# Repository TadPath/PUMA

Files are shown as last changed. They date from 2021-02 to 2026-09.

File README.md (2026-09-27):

PUMA 3D PRINTED MULTIMODALITY MICROSCOPE 
========================================

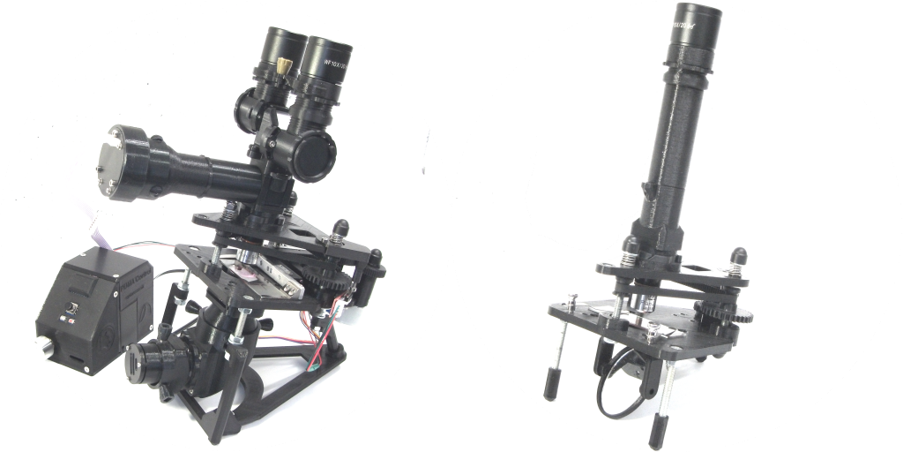
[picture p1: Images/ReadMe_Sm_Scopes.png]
PUMA Example Scopes

---

# **New** :arrow_right: **CNC Stage** 

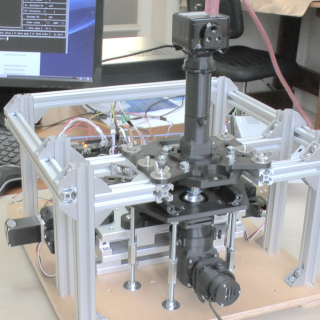
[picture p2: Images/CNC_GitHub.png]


I developed a full XYZ precision CNC stage for PUMA (completed in 2026) and I will be making videos to show you how you can make and use it. The CNC stage uses a 'standard' CNC system i.e. NEMA bipolar motors, optical limit switches, TMC2209 digital stepper drivers on a modified RAMPS 1.4 board (as opposed to 'custom PCBs'), desktop computer control with a 'standard' CNC breakout board (as opposed to being dependent on the RPi), ability to use 'standard' CNC software like Marlin, Klipper, GRBL, Linux CNC, etc. - but also controllable by my own [PARDUS control system](https://codeberg.org/TadPath/PARDUS).<br/>
If you want to follow the progress of this then [head over to the latest posts on my Patreon page](https://www.patreon.com/c/PUMAMicroscope).<br/>
<br/>
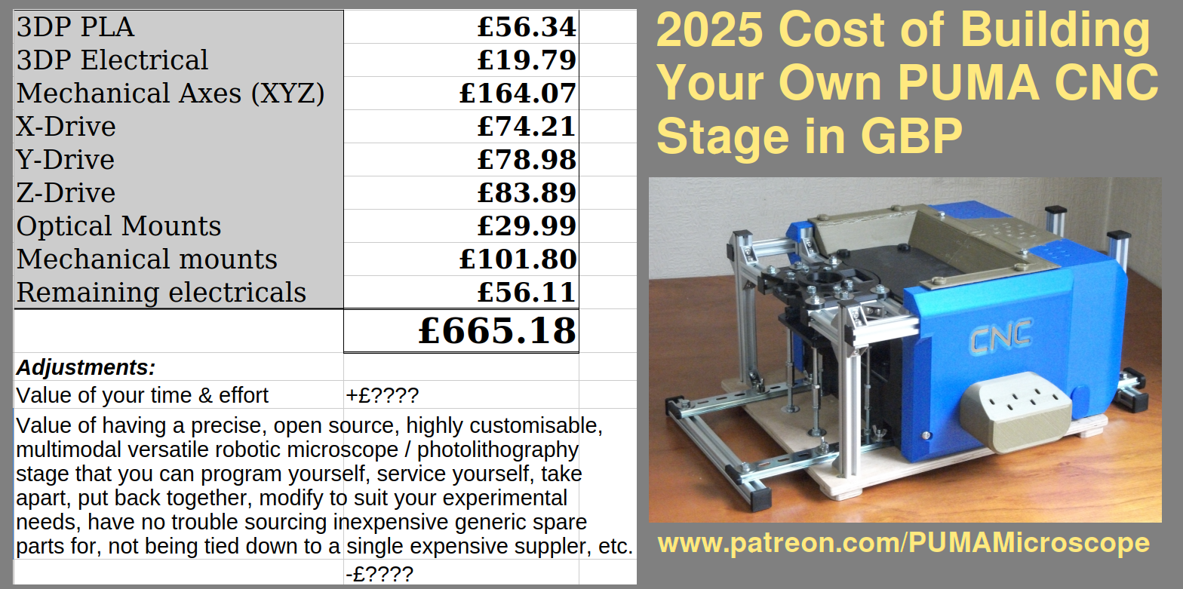
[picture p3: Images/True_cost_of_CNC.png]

<br/>

----------------------------------------------------------------

## :warning: **NOTE TO ALL MAKERS**

The 2021 (v.1.0.0) release is out of date - only use models from the main branch if building a scope. Also, the latest (v1.0 RC ) version of FreeCAD has bugs which make it difficult or impossible to edit the FreeCAD models for PUMA at this time. Please use v0.2 FreeCAD if you experience problems editing the models. Issues have been raised with the FreeCAD team here: [Boolean Issue](https://github.com/FreeCAD/FreeCAD/issues/17338) , 
[Chamfer/Fillet Issue](https://github.com/FreeCAD/FreeCAD/issues/18372) . I have described a workaround for those who just want to get printable files of the models - see the [ReadMe](https://github.com/TadPath/PUMA/tree/main/FreeCAD#readme) in the FreeCAD folder of this repository for details.

----------------------------------------------------------------

* **PUMA has a [Dedicated YouTube channel](https://www.youtube.com/channel/UCOvBahuVgEmLB5ycQEsgEnQ)** where you can see video construction guides, usage tutorials and more. Please subscribe to the channel to get notified of new videos. By subscribing you will be supporting the future development of the PUMA project.

* **Quick Start Guide** : There is also a [PUMA Quick Start Guide PDF document](docs/QuickStartGuide.pdf)  which guides you through the process of making your first PUMA microscope. It tells you exactly what models to print and what hardware to get with extra links to example sellers online.

* **PUMA Scopes are commercially available from [OptArc.co.uk](https://www.optarc.co.uk/).** For those who want to use PUMA but are not interested in doing all the DIY construction, we can now supply ready-made PUMA scopes via our online store. Proceeds go towards supporting the development of PUMA. OptArc also provides free user manuals on its [Support pages](https://www.optarc.co.uk/support/).

* **Funding**. This is a personal project I do in my own time. There is no government / industry / agency grant funding. If you like this work and want to support its continuing development please consider: 1. [Becoming a Patron](https://www.patreon.com/PUMAMicroscope), 2. [Donating to OptArc via PayPal](https://www.paypal.com/donate/?hosted_button_id=NPMYJKJATDLQ4) *Thank you*.

---

This project is released under the following licenses:

 For source code (including CAD files, STL files and computer programs) and compiled code: the GNU GENERAL PUBLIC LICENSE Version 3
 
 For documentation: the GNU Free Documentation License, Version 1.3
 
 GitHub Repository DOI: 

 PUMA is published in the Journal of Microscopy, see DOI:[10.1111/jmi.13043](https://doi.org/10.1111/jmi.13043)
                       
Introduction
------------
PUMA is an Open Source (GPL v3.0) 3D printed light microscope system - backed up by a peer-reviewed paper in the Journal of Microscopy - designed for direct eye observations and ultra-portability with advanced options for digital imaging, measurements and computer control. The name PUMA is an acronym of some of its most important distinguishing features: [P]ortable, [U]pgradeable, [M]odular, [A]ffordable

As a medical pathologist (now retired from clinical work but still active in research) I use high quality optical microscopes routinely. I know what a great optical image they provide, how comfortable they are to look down and also how horrendously EXPENSIVE they are to buy and maintain putting them beyond reach of most people. I designed the PUMA scope to make such a high quality optical viewing microscopy experience available to people without such generous funding resources and also to teach people about the prinicples of optical microscopy - what better way to re-inforce theoretical learning than to be able to build a high quality microscope from scratch?

Most 3D printed open source microscopes I have seen appear to be either toys or low power inspection scopes and/or they are designed to be used as camera scopes with a web-cam / PiCam or smartphone. Many also seem to be novel re-inventions of the microscope that would seem unfamiliar to people used to operating a traditional laboratory bench top microscope - that doesn't mean they are not useful in their own way of course.

PUMA is an open source 3D printed traditional-style direct vision microscope designed as a professional benchtop microscope of familiar design but made with inexpensive materials and 3D printing - and made truly portable for field work. Here are its main features:

* It can use professional quality standard microscope optics including high numerical aperture (NA) objectives - up to oil immersion with NA = 1.25 (e.g. 1000x total magnification). That is enough to see bacterial morphology, individual cell chromosomes and sub-chromosomal details (such as FISH signals and banding). 
* It is truly portable (no mains, smartphone, PC or monitor required).
* It is a multi-modal scope with options for: bright field, fluorescence, dark ground, epi-illumination, polarisation and phase contrast. 
* It has advanced options not usually found on even expensive lab research scopes such as an augmented reality heads-up display and a computer-controlled spatial light modulator for optical Fourier filtration.
* It is not restricted to using a camera, computer and screen for observations (although these may all be used, if desired).
* It is designed to be easily used by those already familiar with standard bench-top microscopes - PUMA does NOT seek to 're-invent' the microscope.
* It is designed to be fully DIY for those who want to have the greatest cost savings - and only uses widely available standard parts. However, for those not interested in DIY, PUMA is also commercially available ready-made from [OptArc.co.uk](https://www.optarc.co.uk/).

Example Images from PUMA
------------------------
The pictures below were taken with a wide field camera on top of an eyepiece to show the whole field of view (except that the last image is cropped). The first row from left to right shows: Bright field Kohler illumination x100 oil immersion objective H&E (chronic inflammation), trans-polarisation through crossed polars x40 objective H&E (striated muscle of tongue), epifluorescence x40 objective fluorescein stain (*Sonchus* flower bud and pollen grains). The bottom row from left to right shows: Epi-illumination through crossed polars x4 objective (circuit board), dark ground microscopy x10 objective unstained section (colon), Schlieren phase contrast x100 oil immersion objective using the spatial light modulator (colonic crypt cells - note the distinct mucigen granules in the goblet cells).

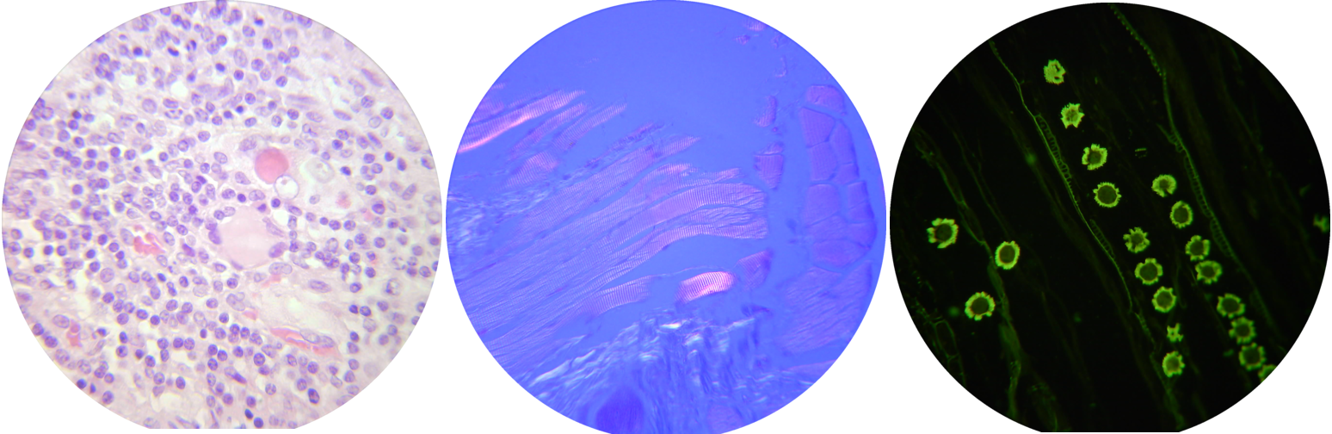
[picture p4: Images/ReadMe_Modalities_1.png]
PUMA Example Modalities 1

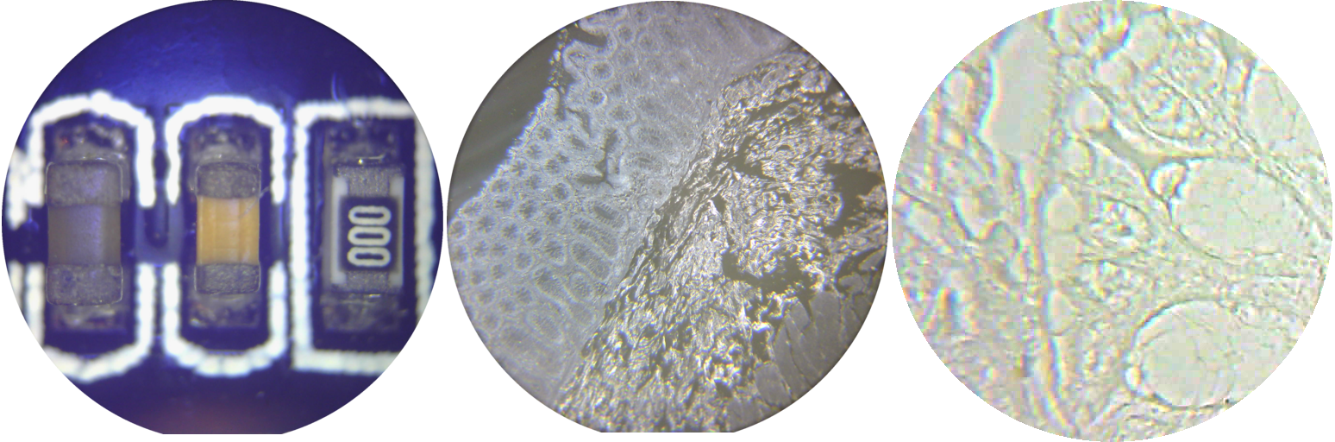
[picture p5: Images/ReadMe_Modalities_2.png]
PUMA Example Modalities 2


Advantages
----------

PORTABLE: PUMA is totally portable. Not only is it small and lightweight but it does NOT require a computer, smart phone, camera or PC monitor to operate. It does have advanced options including an in-built computer and motorised Z-stage but even those options are driven by a small dedicated battery-operated control console. There is no need to plug into the mains. Solar powered battery chargers can be used to keep standard batteries topped up (AA and 9V batteries can be used). So PUMA can be used for extended periods in remote places without mains electricity and without internet connectivity. It can be quickly 'field-stripped' for transport without tools and likewise reassembled. There is also the option to use a mains power adapter if full portability is not required.

UPGRADEABLE and MODULAR: Like many professional series of laboratory microscopes, PUMA is modular. You can use it as a simple - but high  quality - monocular microscope with an adjustable mirror for illumination (so not requiring any electronics at all) - all the way through to an all-singing, all-dancing trinocular scope with full Kohler illumination and an augmented reality unit for a heads up display of its integrated computer allowing for digital measurements and much more - while still being fully portable. Many other configurations are also possible e.g. epi-illuminated, fluorescence, dark ground, polarisation, etc. However, PUMA uses the concept of modularity to enhance its role as a standard benchtop observational microscope and to make it possible to upgrade without duplicating existing 3D printed parts and to switch modalities with the greatest ease and simplicity. No attempt has been made to make PUMA a general optical bench. 

AFFORDABLE and OPEN SOURCE: All aspects of the PUMA are open source and not monopolised behind paywalls and patents. As a 3D-printed project it is designed to be built and customised by anyone with access to 3D printing  and uses standard fixtures and fittings that are available form a variety of retail outlets like Amazon, eBay and AliExpress. Even the high quality optics can be purchased inexpensively form these general outlets - you don't need to buy any component from a specialist university optics supplier or a major microscope manufacturer to get a professional quality optical experience.

Costs to build a PUMA scope  (valid at around June 2021) for three typical configs are given in the table below. Config 1 is a basic monocular scope with mirror for illumination as shown in above figure on the right. Config 2 is for a practical epi-fluorescence scope with LED illumination and an XY mechanical Vernier slide holder. Config 3 is for an advanced trinocular scope with LED Kohler illumination, the AR HUD projector and controller, XY Vernier slide holder and stepper motor focus control similar to the above figure on the left but with the addition of a trinocular port and eyepiece. Costs are in GB Pounds, you can convert to USD or whatever currency is local to you):

| Materials   | Config 1 | Config 2 | Config 3 |
| ---------   | -------- | -------- | -------- |
| PLA plastic | £4.12    | £6.26    | £13.88   |
| Optics      | £25.60   | £46.30   | £97.64   |
| Electronics/mechanics | £17.45 | £26.80 | £61.37 |
| **Totals using DIY printing** | **£47.17** | **£79.36** | **£173.18** |

DIY: Great care has been taken in the design to ensure the whole scope with all its advanced options can be built by anyone with standard tools and only moderate DIY skills. There is no need to print/etch/drill custom circuit boards and only standard fixings are used - screws and washers that can be purchased cheaply almost anywhere. Even the most advanced optional electronic components can be made with just basic soldering skills and tripad prototyping board. A single Arduino Nano is used as the basis for on-board computing.

RMS STANDARD: The scope accepts RMS standard objectives so you can use very high quality optics such as objectives from the Olympus BH series or old Zeiss / Leitz objectives that can be purchased second hand on eBay or can be found spare in many labs now that most microscopes have gone over to infinity optics. The mechanical tube length of PUMA is 160 mm (or 170 mm with a 3D printed ocular extension adapter that is also part of the PUMA standard). One of the reasons PUMA is so small and lightweight and inexpensive to make is that I designed it to work entirely in this length without any tube extension lenses - so even the complex binocular head adapter (and trinocular) all work in this short mechanical length.

INFINITY OPTICS AND C-MOUNT: PUMA works best with 160 or 170 mm tube length objectives. With the addition of an inexpensive tube lens more modern infinity objectives may also be used including those with a larger thread mount such as the Leica NPlan series - although the image quality will not be so good due to the proprietary nature of the corrections used in such objectives. This infinity option is therefore provided, but not recommended. I am currently working on a more dedicated high quality infinity optics adapter so watch this space for updates.

HIGH EYE POINT OCULARS: Some other 3D printed microscopes were designed to be used with camera, computer and display screen to produce an image - if they use a wide field ocular it is mostly so that they can place a smartphone in front of it rather than it being positioned ergonomically for a human eye. The PUMA is designed as a direct vision scope which will take standard professional quality high eye point eyepieces to allow clear and wide angled field of view even for spectacle wearers. This allows the user to instantly access the widest possible field of view and highest possible resolution in a portable design that is ergonomic for a human observer. For scopes that are dependent on cameras the image size and quality is limited by the size and quality of the available camera chip and computer screen. To get an equivalent large wide angled quality view with a camera scope, you would need a very large monitor (so not portable) and the resolution and colour would never be as good as direct human vision.
PUMA can be used in monocular (standard and ergonomic variable angle options), binocular and trinocular modes. As a first for 3D printed scopes, PUMA also has a live 'double-header' mode so two people can look down the scope simultaneously for live discussion / teaching - without the need for a camera / monitor system. PUMA was designed for human observers to look down the tubes - this was a primary design objective - not an optional afterthought.

CAMERA OPTIONS: Of course PUMA has the option of attaching a camera if you like - in fact you can attach up to 3 cameras simultaneously - so as to provide all the benefits of digital imaging, recording and broadcasting - but this is an option, not a necessary or prime requirement to use the scope. Furthermore the type and make of camera is not restricted. Any camera that can mount on a standard professional laboratory scope can also be mounted to PUMA. So specialist research can be conducted if this requires specialist C-mount scientific cameras. Even smartphone cameras can be used via widely commercially available smartphone to eyepiece adapters.

HIGH QUALITY ILLUMINATION: Full Kohler illumination with access to illuminated field and illuminating aperture stops is part of the PUMA standard together with an Abbe-type condenser unit. There are also simpler illumination schemes for those who do not need such high NA imaging. There are also epi-illumination, fluorescence illumination, dark ground and polarisation (both trans and epi) options as well as simple mirror-based illumination. Fourier-plane phase contrast is also possible by condenser aperture shaping (so without the need for special phase contrast objectives and tube phase rings). The illumination system was such a major component of the PUMA project that is was given its own development name - the 'Dominus Illumination System' (or just 'Dominus' for short).

SPATIAL LIGHT MODULATOR (SLM): Unlike many commercially available professional scopes - whose condenser aperture can only be opened and closed in a circular pattern or use a central blocking spot for darkfield mode - the PUMA has a highly flexible condenser aperture. This can be made to be of any arbitrary pattern using either standard physical aperture templates (see first row image below showing the manual filter system on the left with some 3D printed layered template filters in situ) or the PUMA SLM - a transparent TFT 240x240 pixel display unit that can be programmed to have any arbitrary pattern on that pixel grid in various colours and shades of grey so not limited to black / white all-or-nothing transmission. The pictures below show the SLM in front of a fluorescent strip light. The top image shows the SLM switched off (middle) and with its boot-up screen (right). The lower row of images shows some example simple apertures for dark ground microscopy (left) and Schlieren phase contrast (middle and right). This makes condenser-based phase contrast simple to achieve as well as provide a basis for Fourier ptychography, Fourier tomographic depth scanning and other Fourier optics methods. One can even program the aperture to modulate according to the optical structure of the specimen currently being viewed via camera feedback so as to have 'object aware' aperture optimisation.

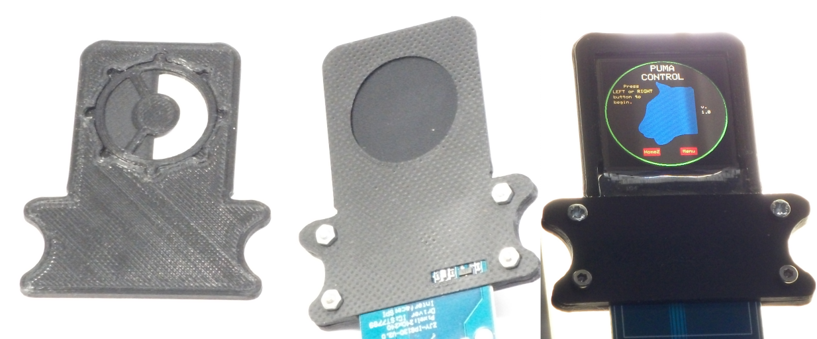
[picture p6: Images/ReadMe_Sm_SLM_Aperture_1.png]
PUMA Condenser Apertures, manual and electronic SLM


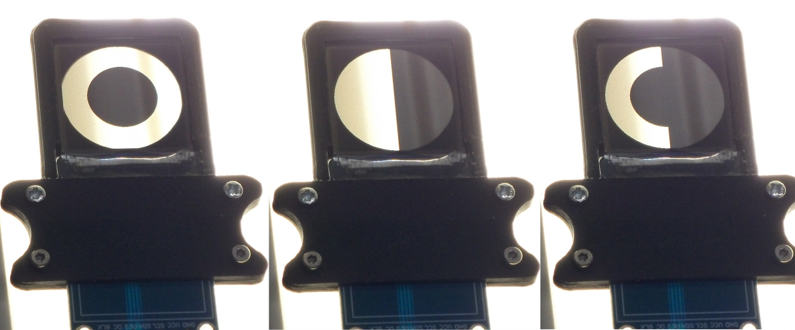
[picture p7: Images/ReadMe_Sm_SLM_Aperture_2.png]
PUMA Examples of SLM Aperture Patterns


MOTORISED FOCUS OPTION: There is an option to use a motor for focussing which gives greater stability and accuracy to the focus mechanism. A full precision XYZ CNC motorised stage option is currently under development and you can follow the progress of that on my [Patreon page](https://www.patreon.com/PUMAMicroscope)

AUGMENTED REALITY (AR) HEADS-UP DISPLAY (HUD): Another first for 3D printed microscopes (to the best of our knowledge) is the unique PUMA AR projector that allows a digital HUD to be superimposed on the live optical image (see example picture below). This allows many advanced features such as an interactive pointer (useful for teaching and demos), an accurate timer (useful for analysis of live specimen events), the superimposition of many custom grids and graticules (for measurements) and scale bars (for teaching and making scientific publication-ready illustrations). The AR HUD also provides for the interactive measurement of calibrated line and boundary lengths, angles and particle counts amongst other things. All of this is controlled by the portable battery-powered PUMA Control Console using an integrated microprocessor (Arduino Nano) so no mains power source or separate display screen, camera, frame grabber or computer is needed (as would be the case for other microscopes that may provide such digital interactive measurements). A reason why PUMA may be the first 3D printed scope to have an AR HUD option is that other 3D printed microscopes to date have been designed primarily as camera scopes rather than direct vision scopes.
Specialist HUD AR units have been designed and are commercially available for standard lab microscopes such as Zeiss and Olympus but these cost several thousands of pounds just for the adapter, let alone the scope, putting them out of economic reach of most people and they are certainly not portable.

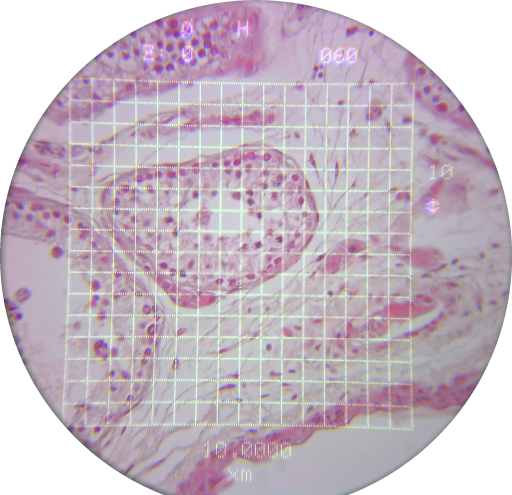
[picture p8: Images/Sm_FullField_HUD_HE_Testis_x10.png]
PUMA Examples of HUD


EDUCATIONAL VALUE: Being open source and 3D printed, together with its standard traditional upright optical design, PUMA also serves as an educational asset to those interested in learning the optics and physics of compound microscopy as well as those wishing to customise and experiment with the optical path of a microscope e.g. to develop novel imaging modalities and perform bespoke imaging experiments. This would be much harder or more expensive to do with a current commercial scope from one of the major professional microscope manufacturers. The design principles developed for PUMA can also be educational in instructing and inspiring those wishing to develop more general 3D printed optical instruments. Thus PUMA has a wide educational reach even beyond those making direct microscopical observations.

STURDY Z-STAGE: The PUMA Z-stage is based on the thread and timing belt mechanism used by 3D printers themselves. This allows it to move the whole above-stage relatively heavy optical assembly very precisely (something that flexure-based 3D printed stages are not currently capable of).

STANDARD XY STAGE: The PUMA specimen stage is of a familiar design using standard stage clips or a standard XY mechanical caliper to hold and manipulate a standard microscope slide over its full range of motion (more than 50 x 25 mm). This allows a standard microscope slide to be screened across its whole viewable area as professional biological microscopists will be used to. PUMA makes no attempt to re-invent the microscope stage using 3D printing. There are also additional fixing holes on the stage for possible future upgrades such as a live cell imaging chamber attachment.

ADJUSTABLE LEGS: The legs/stand system can be configured for a 35 degree slant of the scope (as shown in the figures above) for a more ergonomical viewing angle of fixed angle ocular tubes or, with a simple hind leg extension, it may be configured to keep the stage level (for imaging live cells in fluid, for example).

Limitations
-----------

Of course a 3D printed, plastic-bodied microscope will have limitations compared to all-metal precision engineered research scopes. The main limitations of the PUMA scope are:
1. PUMA is for research and educational use only. The PUMA system does not currently have any licenses or approvals from regulatory bodies in any country for use in clinical or veterinary diagnosis and/or treatment.
2. PUMA can only accept one objective at a time. In order to change the objective you must physically unscrew the existing one and screw in the new one - there is no turret mechanism.
3. Limitations of stability due to lightweight plastic construction. Especially at high magnification (e.g. x40 objective or x100 oil objective) the image will noticeably wobble if the scope or the desk is touched or otherwise disturbed during observation. Also, the focus mechanism displays some elastic backlash. This can be compensated for by varying your focus technique but this can take time to get used to for those who are used to the smooth focus of precision metal milled rack-and-pinion focussing. The motorised stage option of PUMA helps reduce both these limitations significantly. 
4. Sample size limit. The tripost architecture of the main stage limits the size of specimen that may be examined. There is no problem examining a standard microscope slide (25 x 75 mm) but larger objects such as some larger Petri dishes and cell culture bottles will not fit on the stage.
5. The PUMA standard for the illumination system employs off-the-shelf mass-produced inexpensive glass moulded aspheric condenser lenses to build a quite complex optical assembly (i.e. Kohler illumination and Abbe condenser). Because these are not custom designed, precision ground and highly corrected - as you would get with much more expensive lab microscopes - the PUMA Kohler setup is more fiddly to align and not as accurate as with expensive research scopes. Nonetheless the PUMA Kohler system is actually very usable and gives a good clean image to high numerical aperture - including for oil immersion.
6. 3D printing is a slow process - it takes 30 hours of printing just to make the parts for the simplest PUMA scope and >100 hours for some of the more complex configurations. Once printed, many components need to be cleaned up to remove any stray plastic then manually assembled. So although it can be quite cost effective to do this yourself if you already have printing facilities, a significant commitment of your time and skilled labour will be required. 
7. Although not a limitation of the scope itself, this seems like an appropriate place to emphasise that the optical image quality can only be as good as the quality of the optics used. If you use an Olympus SPlan objective and Olympus WK 10x/20L-H eyepiece (which you can use with PUMA) then you can get the optical image quality of a professional Olympus BH-2 microscope. However, if you use a cheap plastic toy RMS objective costing £5 from AliExpress and a cheap plastic toy eyepiece then you will get the optical viewing experience of a cheap plastic toy microscope.

PJT

First Written: 24.02.2021

Last Edit: 27.09.2026

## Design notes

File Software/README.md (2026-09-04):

PUMA Software Repository
========================

This folder contains the software associated with the PUMA microscope project. This is only for software that does not link to the [PARDUS robotics control system](https://codeberg.org/TadPath/PARDUS)
Any software or firmware that designed to be used with PARDUS will be hosted on the [Codeberg site for PARDUS](https://codeberg.org/TadPath/PARDUS). That includes all software related to the PUMA Aperta system.

PUMA Control
------------
The 'PUMA_Control' software is a package for Arduino Nano that serves the PUMA Control Console including the heads-up display (HUD) of the microscope and some basic aperture generation tools for the spatial light modulator (SLM). This includes interactive measurement functions, a timer, a pointer, various graticule overlays, Z-motor control, a real-time lamp current meter and other facilities.

PJT 04.09.2026

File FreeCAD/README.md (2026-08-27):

PUMA CAD Files
==============

Introduction
------------
These are the source CAD files for the PUMA 3D-Printable Microscope Project. The files for the CNC stage and PUMA Aperta were made with version 1.1.3 but the other files were made with older, pre v1.0 FreeCAD and need special treatment as follows. **Before opening any of these FreeCAD files into FreeCAD v1.0 or later - whether to edit or just to make printable files like STL or 3mf - please see the 'Issues with FreeCAD v1.0' notes below.** Note that you will need other components in addition to the 3D printed parts represented here to build the modules. For example, screws and lenses. Details are given the the construction documentation and YouTube videos. Also note that I use the Fasteners Workbench add-on for FreeCAD which you may need to properly view some files. You can install the Fasteners Workbench by following the instructions given here: https://wiki.freecadweb.org/Fasteners_Workbench . 

Issues with FreeCAD v1.0
------------------------
These CAD files were made in FreeCAD v. 0.19 and v. 0.2.0.1 using 64 bit Arch Linux. 
FreeCAD v1.0 currently (2024-2025) has some bugs which make it impossible to edit all the models without crashing and may corrupt some of the model features if you try to 'recompute' the models in these versions of FreeCAD. Issues have been raised with the FreeCAD team here: [Boolean Issue](https://github.com/FreeCAD/FreeCAD/issues/17338) , [Chamfer/Fillet Issue](https://github.com/FreeCAD/FreeCAD/issues/18372) . So please take the following steps to avoid printing faulty models:
1. If you want to edit a model, please continue to use v0.2 of FreeCAD till the bugs / incompatibilties with V1.0 are ironed out.
2. If you just want to create a printable file from a model then, when you load the FreeCAD file, do **NOT** 'recompute' the model as suggested by FreeCAD. Instead just select the model and export it as a .3mf file (I recommend using the .3mf format instead of .STL files). You do this by selecting File -> Export (see the figure).

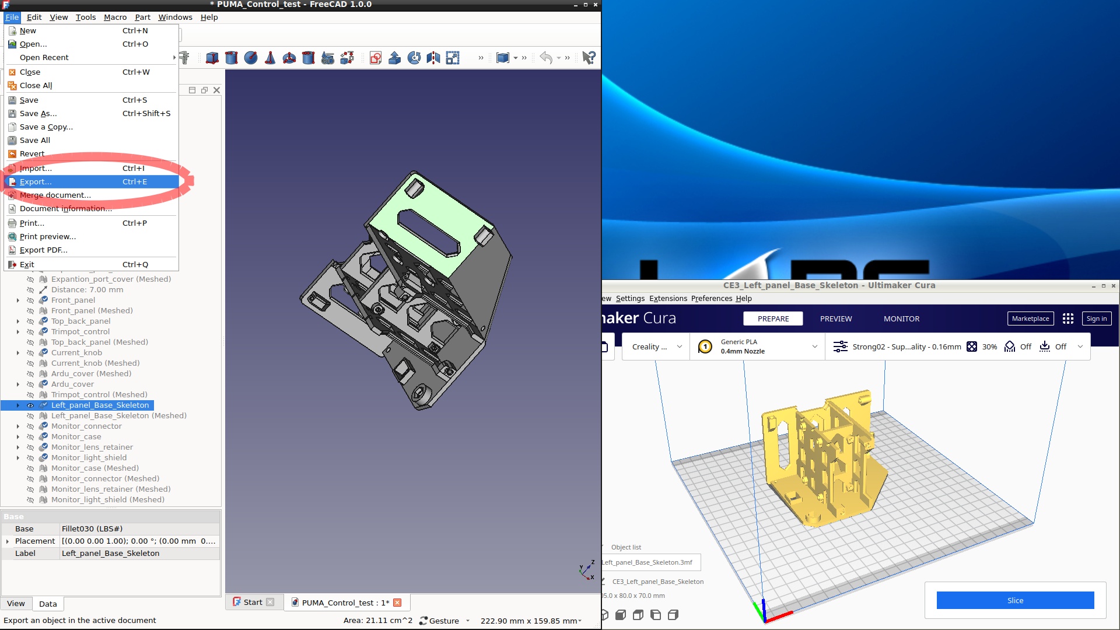
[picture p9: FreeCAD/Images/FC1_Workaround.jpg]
Exporting as .3mf files


Updated Models
--------------
Updates to models that have occurred since the v1.0 release of PUMA are described in the YouTube videos and some are also described in detail below. Many models have been updated since the v1.0 release so please use the models from the current main branch of this GitHub repository when building any part of PUMA.

At the end of this document therr is a summary of what each file contains is given below. For details about the parts and construction of the microscope see the detailed documentation and tutorials.

Updates to the Abbe Condenser Module
------------------------------------
Since making the video on the Abbe condenser it has come to my attention that there are at least 3 variations of 30 mm lens that are sold by different suppliers (shown in the photos below), not all of which are acceptable for use in the condenser module.

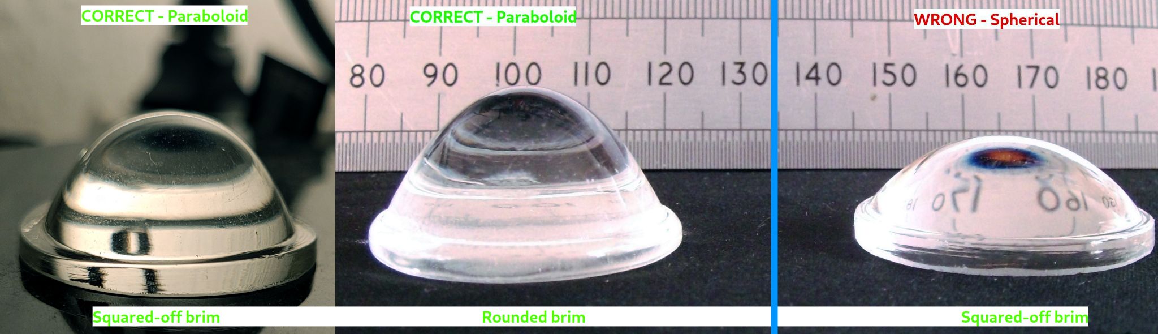
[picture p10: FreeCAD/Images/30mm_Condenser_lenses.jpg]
30mm lens variants


The correct type of lens has the tall paraboloid shape,the shorter spherical lens is not suitable (it has the wrong focal length). However, of the acceptable paraboloid lenses there are two subtypes: one has a base brim with a curved edge to it and one has a base brim with squared off edges. These two require slightly different model parameters to fit well into the DI_Condenser_23_30 housing.
I have modified the condenser 23 30 model to have a 'spring-loaded' receptacle hole for the 30 mm lens which now accommodates any of these lenses and which should also compensate for any slight differences in tolerances between printers and between lenses. The new model also has ejection ports which allow the lenses to be removed and resited without damaging the print.
The previous fixed hole size models have been deleted.
I have also updated the condenser base so as to have a diaphragm which makes it easier to insert IAD filters without undue force (including the delicate electronic TFT screen-based SLM). The condenser attachments for the mirror suspend socket and upper collector have had their top threads truncated by 0.5 mm to ensure they don't protrude on this new aperture diaphragm and impede the insertion of IAD filters.
If you have already successfully built a condenser and have no problems inserting IAD filters then there is no need for you to update anything - the optics of the previous and new versions are not significantly different. If you find you are having problems inserting IAD filters then you may want to swap in the new DI_Condenser_base and use the new DI_Cnd_to_UC / DI_Cnd_mirror_holder_socket connectors as it may help with that.

Summary of Each File
--------------------
**AF51_Accessories**

Free open source accessories for the [OptArc AF51 camera](https://www.optarc.co.uk/products/cameras-2/). This includes the eyepiece clamp (so you can customise it to fit your own eyepieces), the narrow eyepiece adapter (for Zeiss and Reichert eyepieces) and the 'NA_Adapter' which is an adapter that allows the camera to be mounted close up to the back focal plane of the objective in the PUMA microscope so you can image the Fourier plane (as an alternative to using a Bertrand phase telescope).

**AR_Projector**

 The augmented reality projector used to provide a heads-up-display.
 
**Binocular**

 Parts required for the binocular head module of the microscope. Only parts specific to the binocular attachment are in this file. The binocular head module also uses some parts that are common to the monocular head attachment which are not duplicated here - see the file 'Monocular' for those common parts.
 
**Dominus**

 The Dominus Illumination System. This includes the parts required for the various illumination options and modules of the microscope.
 
**FilterBlock**

 These are the parts for that segment of the optical tube of the microscope that goes between the objective quick release receptacle and the ocular head module. It includes two options - a simple filterblock and an advanced filterblock. The simple one has space for two slider filters only. The advanced module has space for 3 slider filters, an optional infinity optics tube lens and a beam splitter / beam joiner cube to allow for epi-illumination, fluorescence, and use of the AR projector.
 
**Focus_Gears**

 The parts needed to make and assemble the geared timing-belt driven Z-stage focus mechanism. Any parts specific to the motorisation option are found in the 'Z_Motor' file, not here.
 
**Legs**

 The various legs used to support the scope in its various configurations.
 
**Monocular**

 Parts for the monocular head. This includes ocular mounting parts that are common to all ocular configurations - monocular, binocular and trinocular.
 
**PUMA_Control**

 Parts for the main PUMA Control Console.
 
**PUMALite**

 Parts for the simpler PUMA Lite console
 
**QuickRelease_v2.0**

 The objective holder which joins to the main optical tube.
 
**Stage**

 The main XYZ stage parts. Use this in conjunction with the 'Focus_Gears' to build a complete PUMA microscope stage mechanuism. This can be motorised in Z using the parts from the 'Z_Motor' file (with motor driven by the PUMA Control Console)
 
**Trinocular**

 The Trinocular / Camera Port tube. This connects to the epi-illumination port of the advanced filterblock to provide an outlet for a third ocular port. This file only contains the tube that connects the parts because the remaining parts are found in other CAD files. For example the 90 degree ocular lens holder is found in the Binocular CAD file. Details of what parts are needed and where to find them are given in the detailed construction documentation.
  
**XY_Stabiliser**

 This is an optional add-on that makes the XY slide mechanical calipers more stable i.e. less prone to wobble and lift. It is not always necessary.

**Z_Motor**

 These are the components required to connect a motor to the microscope stage for motorised focus / Z-motion.

PJT 25.02.2021, Last edit 06.01.2025

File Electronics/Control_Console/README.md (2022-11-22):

PUMA Project: Control Console Specifications and How To Guide
=============================================================  
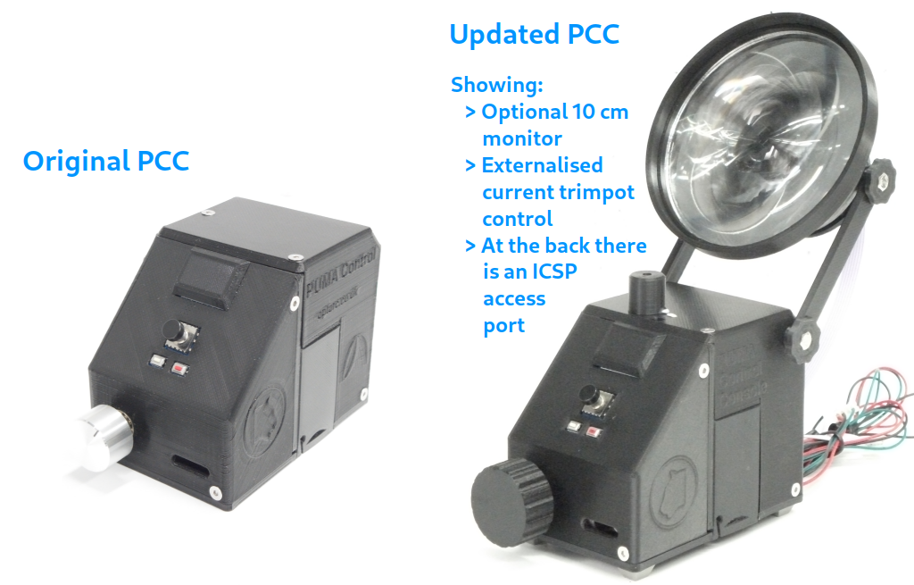
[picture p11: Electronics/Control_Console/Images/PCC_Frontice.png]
PUMA Control_Console
  
This project is released under the following licenses:  
For source code (including CAD files, STL files and computer programs) and compiled code: the GNU GENERAL PUBLIC LICENSE Version 3  
For documentation: the GNU Free Documentation License, Version 1.3  

Introduction
------------
The PUMA Control Console (PCC) is the device (pictured bove) which lets the user control the Z-motor, lamp brightness and TFT displays of the spatial light modulator (SLM) and head-up-display (HUD). A detailed illustrated user manual explaining the hardware and software is available here: [PUMA Control_User_Manual](../../Software/PUMA_Control_Manual.pdf)

A single PCC can only *independently* control one TFT device at a time so can only control the HUD or a SLM at any one time. However, with a specially constructed 'Y' connector cable you *can* drive two TFT's simultaneously but they will show the same image as each other. This may be useful, for example, for you to view the current IAD aperture on the PCC's optional 10 cm monitor at the same time as the SLM TFT is in the microscope.

If all you need is electronic control of the microscope lamp and nothing else then the PCC is overkill. I recommend you use the PUMA Lite console instead which is much easier to build (see the relevant section of the GitHub page for details on the PUMA Lite console).
The PCC uses generic parts that are widely available with the exception of the custom PUMA motherboard. However the motherboard can be made as a DIY project (see the [PUMA Motherboard_HowTo_Guide](../Motherboard/README.md)).
A [video tutorial](https://youtu.be/NZe9j9cfFfs) was made which shows how to construct the PCC. This 'How To' guide gives details of the materials tools and components you need but only sparse assembly instruction - see the video for a more comprehensive illustrated construction guide.

:warning: Safety Warning :warning: 
--------------
This project uses a high current power regulator and power supply. Making wrong connections or failure of components or misuse can cause fire, burns injuries, battery damage (explosion, fire or corrosive chemical leakage) and permenent damage to components and equipment. Only attempt to make this project if you have sufficient electrical enigineering experience or supervision. Read the user manual prior to first use [  [PUMA Control_User_Manual](../../Software/PUMA_Control_Manual.pdf)  ].

Required Components
-------------------
* The following 3D printed parts as specified in the [PUMA 3D_Printing_Guide](../../3D_Printing/PUMA_3D_Printing_Guide.pdf):
    1. All parts in the chapter 'PUMA Control Console'
    2. The part 'PL_Knob.stl' from the 'PUMA Lite' chapter.
* The following pre-assembled PCBs:
    1. PUMA Motherboard
    2. Arduino Nano v.3 microcontroller
    3. ULN2003 stepper controller board (for a 28BYJ48  motor) of the type shown in the below picture.
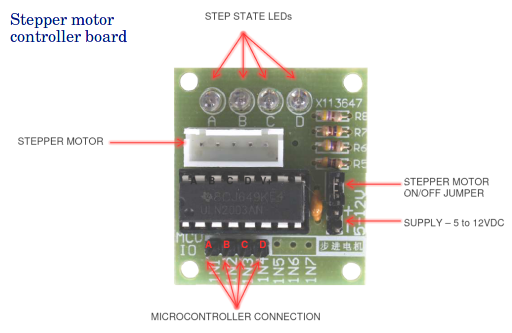
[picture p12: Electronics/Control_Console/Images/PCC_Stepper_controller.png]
PUMA Stepper controller
    
    4. XL4015-based DC-DC step-down buck converter module with both current and voltage regulation of the type shown in the below picture.
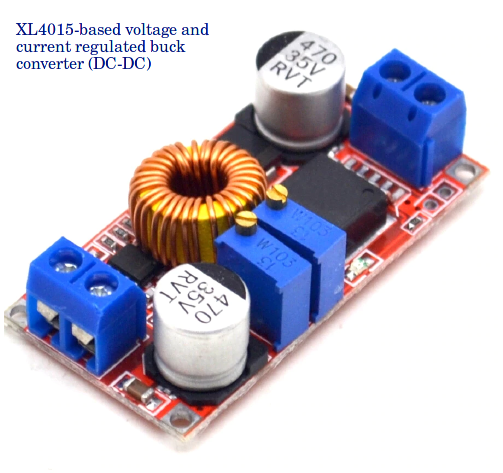
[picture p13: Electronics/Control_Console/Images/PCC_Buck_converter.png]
PUMA Buck converter
    
    5. 5-way joystick navigation button controller for Arduino with two additional push buttons of the type shown in the below picture.
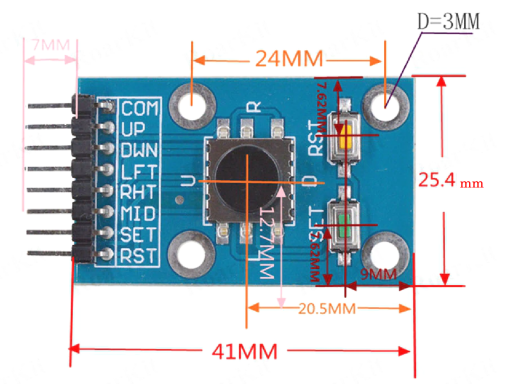
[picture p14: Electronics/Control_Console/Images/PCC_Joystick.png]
PUMA Joystick
    
* A passive piezoelectric sounder buzzer: AT3040 type with a 30 mm diameter, 5.5 mm high enclosure. The enclosure to have two 2 mm fixing holes 35 mm apart. Specifications as shown in the below picture:
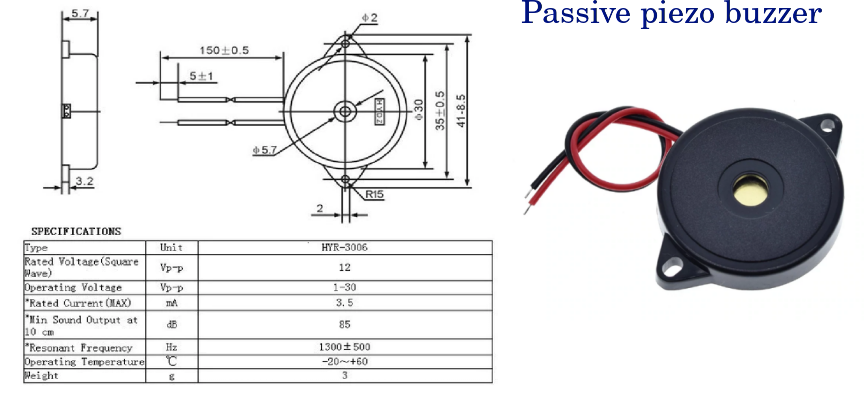
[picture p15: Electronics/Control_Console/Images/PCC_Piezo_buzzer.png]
PUMA Piezo buzzer

* Solder
* Insulated power cable  about 30 to 50 cm long in total. Two connecting wires in this cable (one for positive and one for ground). There is no need for it to be coaxial or shielded. Speaker figure of 8 cable can be used (outer dims ~2.2x4.4 mm, inner core 8 strand copper conductor).
* Phono socket panel mount type
* JST XH double headed connector cables and PCB headers. The cables 20 cm long each. right angled versions of the headers should be used. Examples of the following pin numbers are required: 2 (3 of these), 3, 4 (at least 2), 5, 7, 8 (at least 2)
* Through hole resistor: 5 Ohm, 1%, 1W, Axial
* Precision potentiometer 200 ohm: Wire wound, bushing mount, Bourns 3590s type.
* ON/Off rectangular rocker switch, 10A/125V or 6A/250V, SPST type. Dimensions: Flange (2.05 cm x 1.5 cm), body size (1.8 cm x 1.15 cm) with 0.48 cm wide connector lugs. Switch body height below flange 1.05 cm and connector lug height 0.85 cm.
* Two of 9v PP3-type battery snap connectors with 150 mm leads
* A power supply: Either two 9v batteries (type 6LR61 PP3) or a mains regulated power adapter that can put out 7 to 9 volts regulated DC and at least 1 amp of current with a PP3 connector.
* Solderable spade connectors with insulator covers of sizes 4.8 mm and 2.8 mm (widths).
* Electrical insulation tape.
* Scissors

Optional Dual TFT Y-Cable
-------------------
* It is possible to operate two TFT devices at the same time from a single PCC. However the image on each TFT will be identical to each other. This option is provided to allow you to see the aperture function of an SLM on an external screen to monitor it. It is intended that this option only be used with an SLM (i.e. one of the two TFT screens must be without an LED backlight to avoid drawing too much power from the Arduino). Both TFT screens must be of identical type. Both screens must be connected to the PCC prior to power-up. This option requires a custom splitter cable ('Y'-cable) shown in the figure:

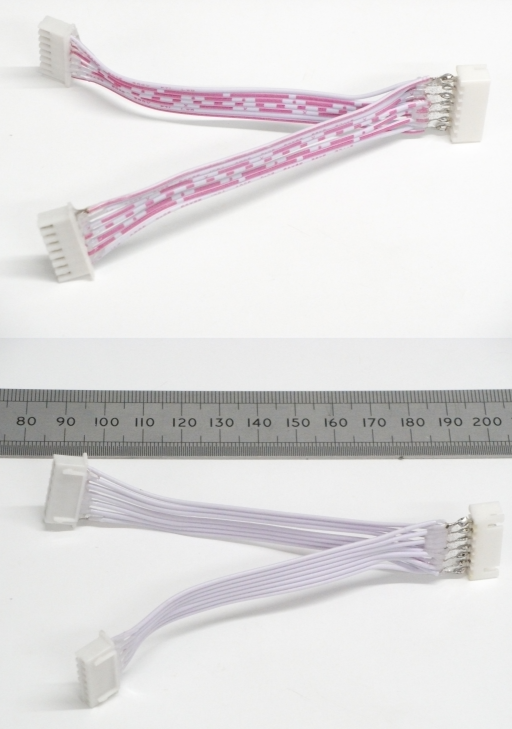
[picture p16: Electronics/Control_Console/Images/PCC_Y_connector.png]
Dual TFT cable

* To make this cable:
1. Cut a 7-pin JST cable in half
2. Strip the insulation from the terminal wires you just cut (remove about 5 mm of insulation from each wire)
3. Twist corresponding bare wire ends together and solder them, one-by-one, taking care to match pin-to-pin (see the figure).
4. Solder each twisted wire to a JST 7 pin male PCB header - taking care that all pins correspond, 1-to-1, 2-to-2, etc.
5. Test the cable by connecting the PCC to the male header of the Y-cable and the two free ends of the Y cable to the two TFT screen - one of which should be an SLM (i.e. without a backlight).
6. If it works (a dual image is seen, synchronised on both TFT screens) then consolidate the connections by covering the soldered connections in epoxy resin as shown in the figure. This is important because those wires are very thin and will quickly break with use.
7. Troubleshooting: You may need to switch power off then on again a few times for the sync signal to 'catch' and 'synchronise' between the two TFT modules. Check all connections - disconnect and re-connect.

Additional Peripherals Required for Testing
-------------------------------------------
* ST7789 240x240 pixel TFT display unit of the kind that will work on 5 volts power and signal supplies (NOT the 3 volt only version - these will not take the 5 volts that the PCC puts out and they will be permanently destroyed if used).
* Stepper motor of the 28BYJ48 type. If using a power supply of 9V or lower then the 5V version of this motor is recommended (the 12V version may not give enough torque to turn the gear system in all circumstances if used with a 9V or lower supply). If using a 12V power supply then the 12V version of this motor is advised (using the 5V version with a 12V supply can result in serious and damaging over-heating of the motor with risk of burns and melting the 3D printed plastic gear). The 12V version of the motor may come with a JST PH connector in which case you will need to adapt the connector to fit JST XH cables e.g. by adding JST XH PCB header to the motor JST PH as shown in the picture below.
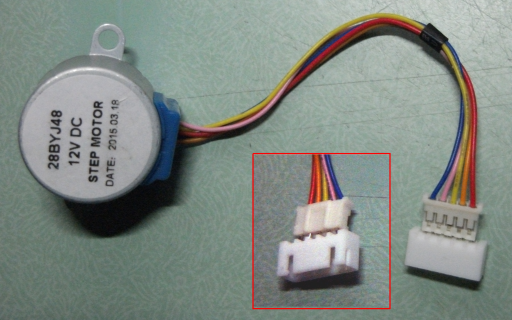
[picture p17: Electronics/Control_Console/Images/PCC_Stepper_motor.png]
PUMA Stepper motor

* Makerbot type endstop limit switch with its cable (customised to fit a 3 pin JST connector as described in the 'How To' document for the PUMA Motherboard. The type of limits switch is as shown below.
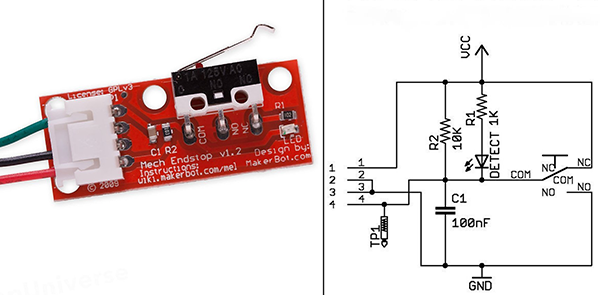
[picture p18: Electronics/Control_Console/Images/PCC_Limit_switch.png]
PUMA Limit switch

* A PUMA microscope LED lamp module

Fixtures and Fittings
---------------------
* All screws are of Allen socket type and made of stainless steel
* The case screws are countersunk. All other screws are socket cap screws.
* The number and type of screws used for each component are given below starting with the component they are to be used for. Lengths refer to the length of the threaded part of the screws (i.e. it does not include the head / socket).
* Case screws: 8x M3, 12 mm long
* Power board: 4x M2, 6 mm long
* Piezo buzzer: 2x M2, 8 mm long
* Motor board: 3x M3, 6 mm long
* Motherboard: 3x (for DIY) or 4x (for PCB) M3, 6 mm long
* Joystick clamp: 1x M3, 5 mm long with an M3 flat form washer
 
Tools
-----
* Wire cutters and wire strippers
* Long nose pliers
* Soldering iron, sponge, stand and fume extractor
* Allen keys (2 mm and 2.5 mm)
* Small Philips head screwdriver
* Multimeter with voltmeter and ammeter capabilities (to more than 1 amp tolerance)

Assembly Procedure
------------------
* See the [video tutorial](https://youtu.be/NZe9j9cfFfs) for detailed illustrations.
* Pre-thread all holes in the casing that are designed to take the thread of a screw. Don't go all the way in and be especially careful of the shallow holes on the front panel otherwise you could deform the external surface or go all the way through with the screw.
* Attach the components to the front compartment. Attack the JST cable to the joystick board then bend this down 45 degrees. Insert the joystick board into its location ensuring it clips over the 4 pegs in the case. Secure the joystick clamp at its threaded end over the joystick.
* Cut a double-headed JST 2-pin cable in half and strip the bare ends for a few mm then connect them to the piezo buzzer with solder and cover this with electrical insulation tape. The connection is made such that the red wire of the buzzer goes to pin 2 of the JST connector.
* Fix the piezo buzzer over the other end of the joystick clamp with its two M2 screws.
* Now we turn our attention to the 200 Ohm lamp brightness control potentiometer. Before fitting this I recommend you bend the end connector to 45 degrees and solder the middle connector to its connecting cable. This connecting cable is made from two components. One is a 10 cm long piece of ordinary insulated wire and the other is a 5 ohm resistor that is soldered to the end of the wire. The other end of the resistor is bent into a loop ready to fit to the power board as we’ll discuss shortly. This resistor is an essential component for safety and controllability of the lamp, so don't skip it.
* Now fix the potentiometer into the front of the casing with its terminals facing up. Note that the hole has flattened regions as does the thread on the bushing so you must site the potentiometer accordingly. Place the fixing washer over the bushing and finally the hex nut. Once the nut is tightened you can add the user-control knob.
* The final item for the front compartment is the motor control board and this is fixed to the wall of the mid-section with these three M3 screws, each 6 mm long.
* Once in place, fix the connecting cables to the motor board. The output cable is a 5-pin cable that goes into this JST connector here and you should bend this down and route it underneath, through the bottom slot in the casing, to the back compartment prior to fixing the motherboard in place. The motor power cable is a 2-pin JST cable that goes on the two power pins of the motor board. The correct orientation is to insert the connector over the pins with the lugs of the JST connector facing *towards* the ULN2003 control chip. Now because this is a 2-pin connector and the piezo buzzer also has a 2-pin connector it’s a good idea to mark the motor connector to distinguish the two. 
* Finally for the front compartment, connect a 4-pin JST cable to the inputs to the ULN2003 control chip and the correct orientation is to insert the cable with the JST lugs facing *away* from the chip.
* We now turn to the lamp power supply (the XL4015-based DC buck converter) which goes into the top part of the mid-compartment. Before fitting the board we need to set the regulated outputs correctly to avoid doing damage to the bulb. To do this, apply a power source to the input pins and get an ammeter and set it to measure up to 20 amps. Apply the ammeter to the output and adjust the current trimmer on the buck converter board – the one closest to the output end of the board – until the current displayed on the meter is 0.33 Amps (i.e. 330 mA).
* Next disconnect your ammeter and change over to a volt-meter measuring in the range of up to 20 volts. Apply the volt meter to he output and adjust the voltage trimmer until the reading is 5.00 volts. 
* The unit is now correctly set, but before we insert it we need to attach the output cables to the board because there’s not enough room to fit them once it’s in place. The output cables are made up in such a way as to connect the output from the board to 3 things:
    1. to the lamp output socket of the console, 
    2. to the lamp brightness potentiometer and also
    3. to the motherboard to enable the continuous monitoring of lamp current. 
* We achieve that connectivity in the following way: Take half a 2-pin JST connector and connect pin 1 directly to the negative / ground output of the power board and this negative output is also connected directly to the lamp output phono socket by a 13 cm long wire with a 4.8 mm spade connector at one end. The other pin of the JST connector is also connected directly to the lamp output phono socket (to the positive terminal this time) by a 20 cm long wire which is marked with a white stripe and also has a 4.8 mm spade connector at one end. In addition, the same pin is also connected to the end connector of the brightness potentiometer by means of a 2.8 mm spade connector but it is not connected to the power board. Instead, the positive output of the power board is connected to the middle lead of the potentiometer by means of the 5 Ohm resistor cable we described earlier (and so the connection to the positive terminal of the lamp and lamp meter are made via the variable resistance of the potentiometer plus the fixed 5 ohm resistor). So connect the looped end of the 5 Ohm resistor to the positive output terminal of the power board. 
* Attach the input cable to the power board by again using half a 2-pin JST cable. For the input, pin 1 connects to the positive terminal.
* We can now insert the power board into the central compartment. To do this first insert all 4 M2 screws through the holes in the board and lift the board as you insert it so that the bottom of the screws don't snag of the risers. Then lower the board into position and fix the screws in their holes.
* We now come to attaching the motherboard in the posterior compartment but before we do that we should first connect the joystick cable to the motherboard because it would be very difficult to do so once the board is in place. Now fix the motherboard to its risers its M3 screws.
* With the motherboard in place we can start to route and connect the cables to it from the front and middle compartments. Connect everything except the main power input to the board. See the Tripad or PCB diagram in the 'Motherboard' 'How To' document for details of what connects where.
* Now prepare the back panel so we can complete the connections. The back panel contains the main power on/off switch and the phono connector that we use as a power output socket for the lamp of the microscope. First bend the pins of the on/off switch to 45 degrees to ensure the connectors fit in the limited space available. Now insert the switch into its rectangular hole in the 3D printed back panel and press down until it clicks in place. Ensure the switch is inserted with the pins bent *away* from the phono connector hole.
* Now insert the outer washer of the phono connector into the round hole from the external aspect then push the main body of the phono connector in. Now from the inside insert the connector washer. Insert the locking nut and tighten it well. Finally, place the small 3D printed M5-type plastic washer over the central connector. This is important to prevent the central spade connector from short-circuiting by touching the negative conducting areas around it. You may need to flatten the the central connector a little with the long nose pliers and this helps retain the plastic washer until we connect the spade connector over it later on.
* Now connect the main power internal connection cables. To do this prepare a set of connected wires by starting with the two 9V battery connectors with their leads joined in parallel – red to red and black to black. Prepared half a 2-pin JST connector cable and connect its free ends as follows: Pin 1 is connected directly to a 4.8 mm spade connector and this goes to one pole of the on-off switch (it doesn't matter which pole). The positive ends of the battery connectors are soldered to another 4.8 mm spade connector and this is connected to the other pole of the on/off switch. Thus when the user closes the switch the positive lead of the input power will be connected to pin 1 of the JST connector. The negative ends of the input power cable are soldered directly to pin 2 of the JST connector.
* Now that you have this power cable arrangement simply insert the power JST connector into the remaining JST plug on the motherboard and pass the battery connectors into the battery compartment area ensuring that their cables are inserted into the grooves in the wall of the cases.
* Complete the wiring by connecting the output lamp spades to the phono connector with the wire coming directly from the lamp brightness potentiometer being connected to the central (positive) terminal. To keep these wires from blocking the Arduino reset pin and power indicator route them around the USB port.
* Ensure all spade connections are tight – crimp them with long nose pliers if they are loose.
* You are now ready to close the case. Push excess cable from the back to the front compartment (because there is more room in the front to accommodate them) and ensure all cables lie in their recessed channels. Then close the front compartment and fix it in place with the countersunk case screws. Next likewise close and secure the back panel with countersunk case screws. While doing this remember to keep all cables away from resting on the walls of the case outside their designated channels including the output cables which must pass through the recess in the bottom of the back panel.
* The Console is now complete and ready for testing. Ensure a power supply with a current rating of at least 1 amp is used and never use anything with great than 12 V output or the Arduino may be permanently damaged.
* Connect JST cables from the Console to the TFT screen, limit switch, PUMA lamp and stepper motor. Ensure the lamp brightness potentiometer is turned clockwise by at least a few whole turns t(o avoid the lamp being started at full power) and switch on.
* If all is well then the red power LED on the Arduino should light immediately as should the microscope lamp. After a few seconds you should hear a double beep on the buzzer indicating that the unit has booted up correctly and the boot up screen should appear on the TFT (this will be a mirror image because the TFT is for the HUD which goes through a mirror transformation by the beamsplitter reflector glass in the advanced filter block before reaching the oculars).
* If the microscope lamp draws too much current (over 350 mA) then the Console will beep 4 times and repeat this until the current is reduced to below this level (by turning the brightness potentiometer clockwise).
* If all starts up well then activate the motor by attempting a 'Z-homing' procedure via the menu options in the GUI (see the PCC User Guide for instructions on how to do this). It doesn't matter if the motor is not connected to a scope - you are only testing that the motor will turn when it is supposed to and you can manually trigger the limit switch to stop it (which is what should happen if all is working as it should be).

Tripping the Lamp Power Regulator
---------------------------------
* It is important to be aware of a problem that can arise relating to the behaviour of the particular XL4015 power regulator board that we use in this unit. This problem occurs when using the unit in a 'low current supply situation'. Examples of a 'low current supply situation' are:
    1. when the batteries are running low or
    2. if only 1x 9v battery is used instead of 2 or 
    3. if an external power source is used that cannot deliver more than 1 amp.
* In any of these circumstances the power regulator may 'trip' if it experiences a sudden drop in input voltage and there is insufficient resistance across its output terminals (which will be the case if the brightness potentiometer is at or near its brightest setting – i.e. its lowest resistance setting).
* By 'Trip' I mean that the output current suddenly becomes unregulated and the LED bulb of the microscope will draw too much current, something like 700 - 800 mA when the bulb’s maximum rating is 330 mA. You may notice this as a sudden increase in brightness of the bulb and there should also be an audible alarm as the console’s internal ammeter detects this and the ammeter reading display in the HUD will change colour to red.
* If this happens you must turn the brightness down immediately using the brightness potentiometer or else the bulb life will be dramatically shortened. Also, if you use batteries, your power supply will be drained even faster.
* It it for this reason that we employ a fixed 5 Ohm resistor in the cable that connects the brightness potentiometer to the power regulator. That 5 Ohm resistor ensures that there is always at least some resistance in the circuit, even when the potentiometer is at its minimum-resistance setting. This is important because the intrinsic resistance of the LED bulb is negligible. So this 5 ohm resistor will limit the current if a trip occurs. Without this resistor the current to the LED could exceed 1 Amp in a trip situation and could blow the LED instantly. It only provides partial protection however, buying you a little time, because 700 - 800 mA is still way too high for this LED and you must act quickly to preserve the life of your bulb by turning the brightness down with the brightness potentiometer.
* A common scenario that induces a 'trip' of the power board is the case when the lamp potentiometer is set at or near full brightness and the Z-motor is activated. Activating the Z motor creates a sudden large current draw on the source and the source voltage can drop causing the power regulator board to trip.
* Another cause is if the unit is switched on with the lamp potentiometer set at or near full brightness because the sudden inrush of current to the bulb causes the input voltage to drop and so trip the power regulator.
* As you can probably work out from the above, one way to minimise the risk of a power board trip is to always keep the bulb brightness potentiometer at a low setting whenever you switch on the unit or activate a motor coil. The latter may not always be possible if you need a bright setting to work with (e.g. crossed polarising or dark field microscopy) – in that case only using a higher current power supply can protect against this issue. 

PJT

First written: 02.03.2021, Last edit 22.11.2022

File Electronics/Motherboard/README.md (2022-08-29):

PUMA Project: Motherboard Specifications and How To Guide
=========================================================

This project is released under the following licenses:

For source code (including CAD files, STL files and computer programs) and compiled code: the GNU GENERAL PUBLIC LICENSE Version 3

For documentation: the GNU Free Documentation License, Version 1.3

The professionally printed motherboard PCB is now available for purchase from the OptArc store here https://www.optarc.co.uk/products/other-components/

Introduction
------------
The PUMA motherboard is an essential component of the PUMA Control Console (PCC) - the device which lets the user control the Z-motor, lamp brightness and TFT displays of the spatial light modulator (SLM) and heads-up-display (HUD).
The motherboard houses the Arduino Nano microcontroller and provides reverse polarity protection for all PCC devices and dedicated IO ports for all peripherals.
A video tutorial was made which shows how to construct the PCC with a ready-prepared motherboard. This How To guide only discusses the construction of the motherboard.
There are two forms of the motherboard:
 1. A DIY form based on ready-made and widely available tripad prototyping board - no printing or etching or micro-drilling required. 
 2. A dedicated PCB design.

The two boards (PCB and DIY) are electronically identical and physically interchangeable. The same circuit diagram applies to both.

Required Components
-------------------
* Tripad electronic prototyping board
* Solder
* Track connecting wire: Single core wire and multicore ribbon cables that can be soldered and that can fit in the prototyping board's holes.
* JST XH PCB connector headers (right angled versions) of the following pin numbers: 2, 3, 4, 7, 8
* 2.54 mm pitch single row female PCB socket pin header connector strip for Arduino. These have an 8.3 mm tall black plastic body. You will need two strips, each with 15 pins.
* P-Channel MOSFET, 78 A, 60 V, 3-Pin TO-220F ON Semiconductor BMS3003-1E
* Through hole resistor: 1K Ohm, 1%, 0.5W, Axial
* Through hole resistor: 430 Ohm, 1%, 0.5W, Axial

Tools
-----
* Wire cutters and wire strippers
* Long nose pliers
* Soldering iron, sponge, stand and fume extractor
* Tools to cut tripad board to size
* Fine tipped permanent marker pens.
* Drill with 3.2 mm bit

Circuit Diagram
---------------
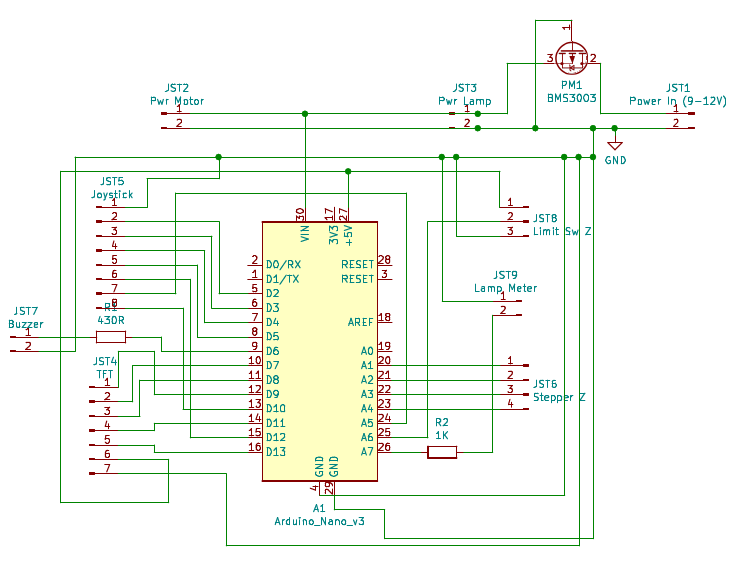
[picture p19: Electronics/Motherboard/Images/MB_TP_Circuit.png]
PUMA Motherboard Circuit


Power Connections
---------------
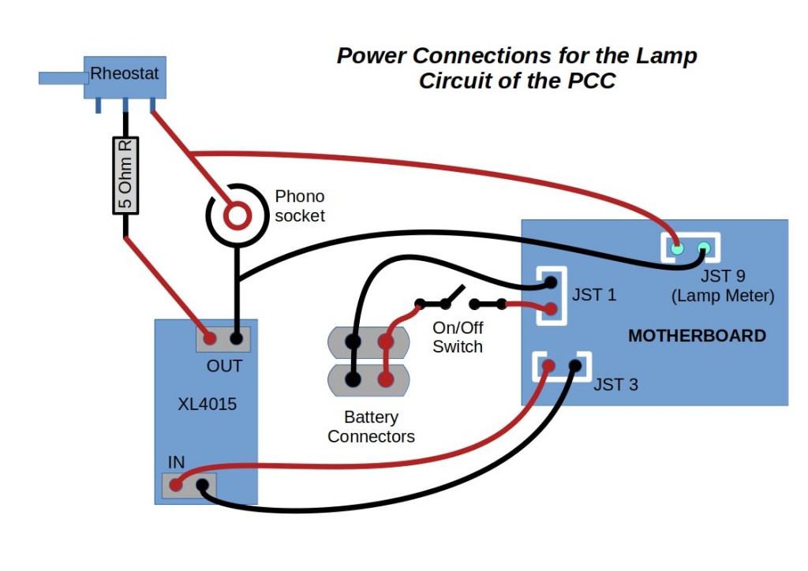
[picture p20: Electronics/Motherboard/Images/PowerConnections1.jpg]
PUMA Power Circuit


Procedure for the DIY Motherboard
---------------------------------
* In the following instructions refer to the below diagram for wiring and placement of components. The diagram is a view from the top / component / non-copper surface. The copper tripads are shown in green as if the board were transparent. Wiring and connections are shown either as thick red lines or thin white lines:

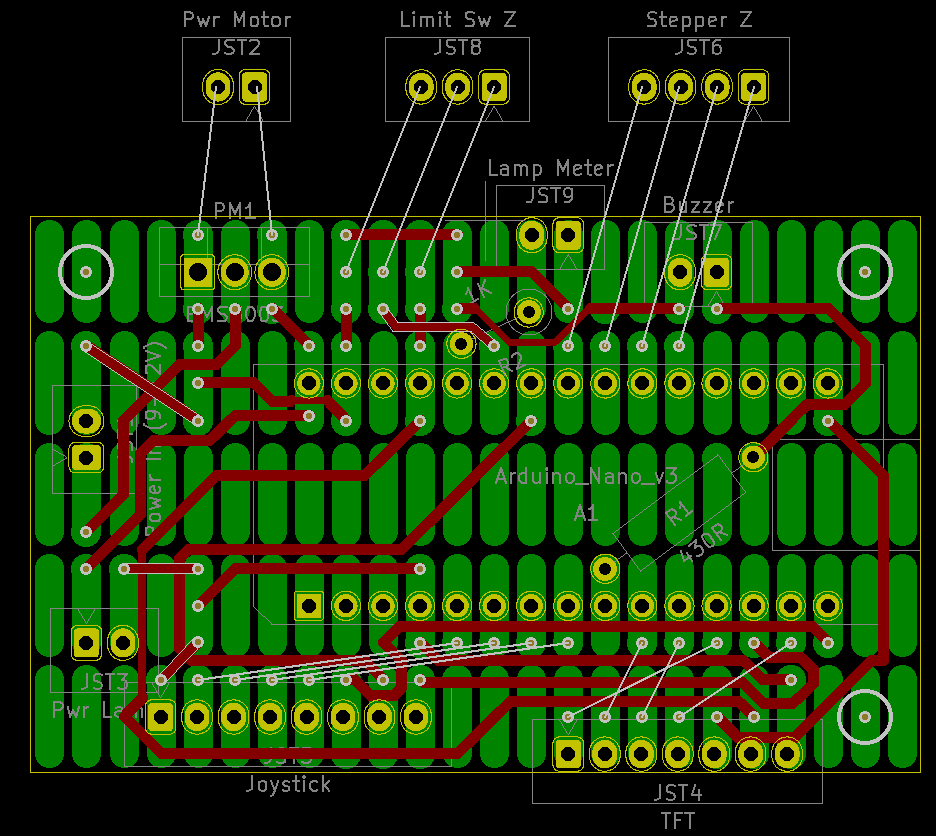
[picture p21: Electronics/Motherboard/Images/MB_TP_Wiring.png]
PUMA Motherboard Tripad Wiring


* Cut a piece of tripad board 5 tripads down by 24 strips across (this comes to about 37 x 61 mm) and enlarge the three corner holes with a 3.2 mm diameter drill bit as shown in the figure below. 
 
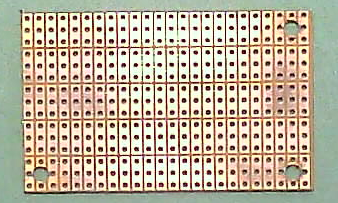
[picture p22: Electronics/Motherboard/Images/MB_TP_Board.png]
PUMA Motherboard Tripad Board

 
* Turn the board over to the non-copper side and mark which pads need interconnecting wires as per the above circuit diagrams. Then proceed to solder linker wires to connect them as in the below picture (wiring is incomplete in the picture and there are some errors so don't copy this picture exactly - be guided by the above wiring schematics).

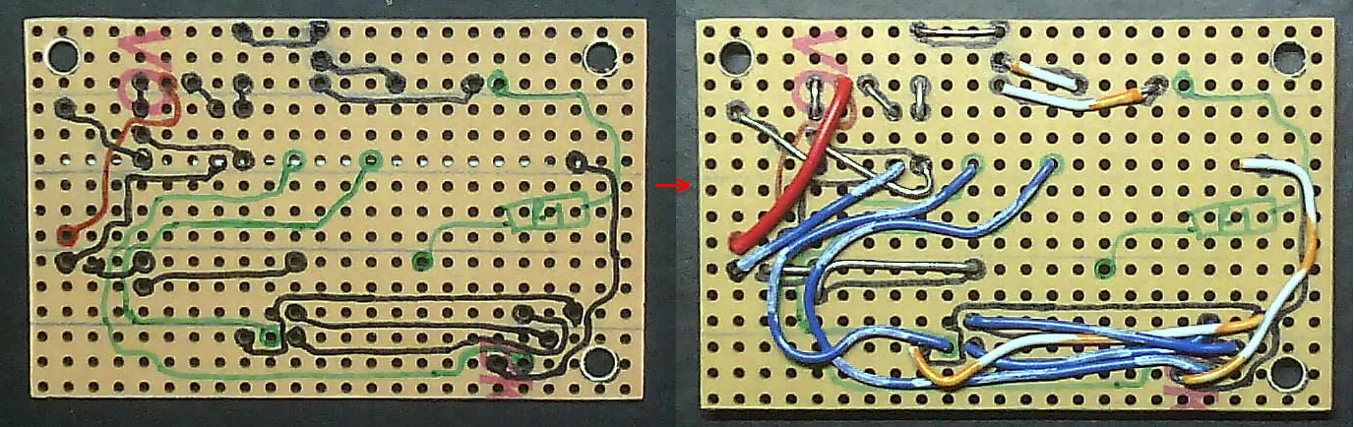
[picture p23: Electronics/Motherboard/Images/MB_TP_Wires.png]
PUMA Motherboard Tripad Link wires


* Next solder in the remaining components and finally insert the Arduino Nano.

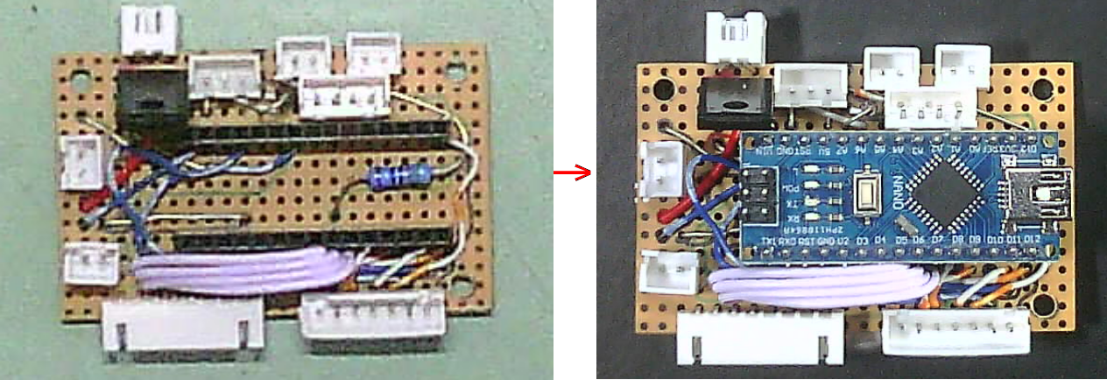
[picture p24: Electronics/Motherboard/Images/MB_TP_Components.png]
PUMA Motherboard Tripad Finishing


* Once the PUMA Control software is loaded onto the Nano you should test it all works with the required peripherals (see the PUMA Control Console specification in the PUMA GitHub repository for specifications as to the required peripherals).

Procedure for the PCB Motherboard
---------------------------------
* This is best made by a professional PCB manufacturing service (as shown below).
* This PCB is commercially avaialable from the OptArc store here https://www.optarc.co.uk/products/other-components/
* The board edge cuts measure 60.96 mm by 44.45 mm so it is slightly larger than the DIY tripad version but the holes are in identical spacing between the two versions and they are interchangeable in the PUMA Control Console (either will fit).
* Make or otherwise obtain a drilled double-sided PCB with the specifications contained in the documents in the KiCAD folder of this repository.
* Solder the components in their places (if not already done for you) and test.

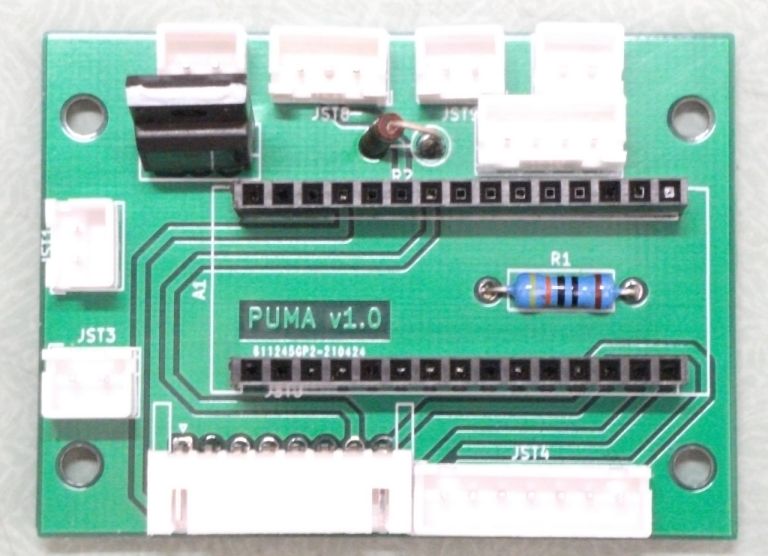
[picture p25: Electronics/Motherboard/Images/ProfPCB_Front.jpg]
PUMA Motherboard PCB Front

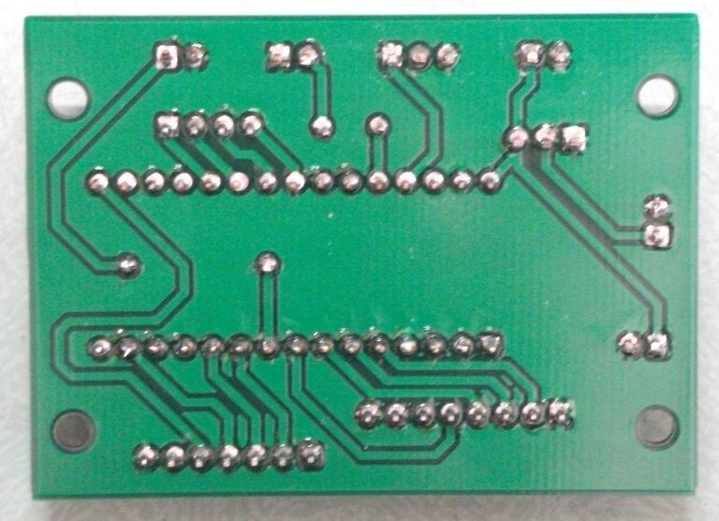
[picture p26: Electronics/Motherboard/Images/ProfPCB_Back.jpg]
PUMA Motherboard PCB_Back

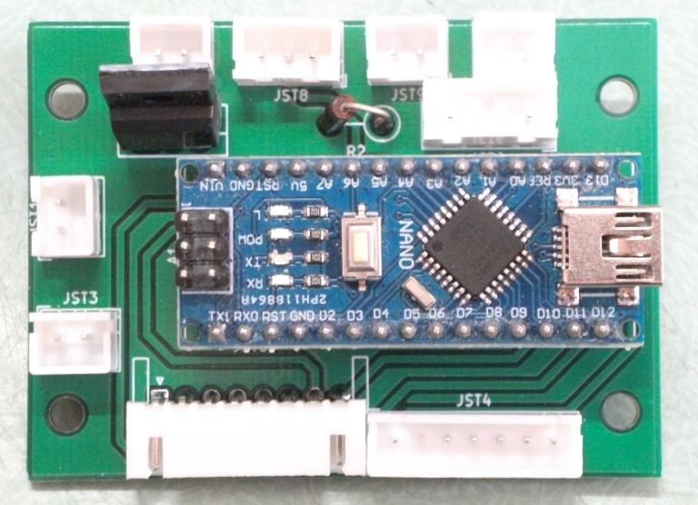
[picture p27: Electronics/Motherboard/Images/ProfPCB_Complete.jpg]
PUMA Motherboard PCB_Finished


Making the Custom Limit Switch Cable
------------------------------------
The limit switches used as part of the motorised Z stage kit come with a 4 pin JST XH connector cable. However they only have three active connections and so only three wires are conveyed with one of the 4 pins of the limit switch JST connector unused. To save space on the motherboard a 3-pin JST header is used. So there is a need to convert this 4-pin connector cable into a 3-pin cable at one end. To do this, cut off the 4 pin JST connector from one end of the limit switch connecting cable and strip the cut ends of the wire bare for a few mm then tin them. Insert the wires into one end of a double-headed 3-pin JST cable in the manner shown in the below figure and fix them in place with a method of your choice (simple electrical insulation tape will work).

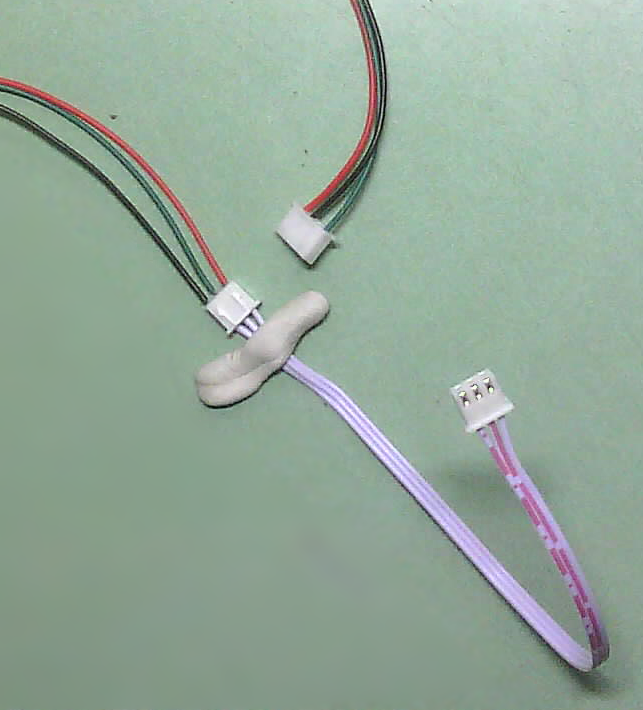
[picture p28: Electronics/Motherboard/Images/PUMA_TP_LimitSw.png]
PUMA Motherboard Limit Switch Cable


PJT

First written: 02.03.2021

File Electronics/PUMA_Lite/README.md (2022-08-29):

PUMA Project: PUMA Lite Control Box How To Guide
================================================
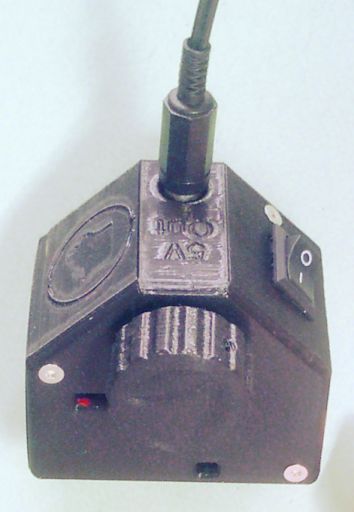
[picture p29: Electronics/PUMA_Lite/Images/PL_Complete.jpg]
PUMA Lite
  
This project is released under the following licenses:

For source code (including CAD files, STL files and computer programs) and compiled code: the GNU GENERAL PUBLIC LICENSE Version 3

For documentation: the GNU Free Documentation License, Version 1.3

Introduction
------------
The PUMA Lite controller (PL) is the device which powers the microscope lamp (only). If you require additional control features (such as the focus motor or AR projector) then you will need the more complex 'PUMA Control Console' (PCC) which does these other things in addition to powering the microscope lamp. The PCC has its own 'How to' guide on this GitHub repository.
The PL can power and control any of the PUMA lamps - for white light or fluorescence - because the different LEDs used for these purposes are electronically cross compatible.

:warning: Safety Warning :warning: 
--------------
This project uses a high current power regulator and power supply. Making wrong connections or failure of components or misuse can cause fire, burns injuries, battery damage (explosion, fire or corrosive chemical leakage) and permenent damage to components and equipment. Only attempt to make this project if you have sufficient electrical enigineering experience or supervision. 

Required Components
-------------------
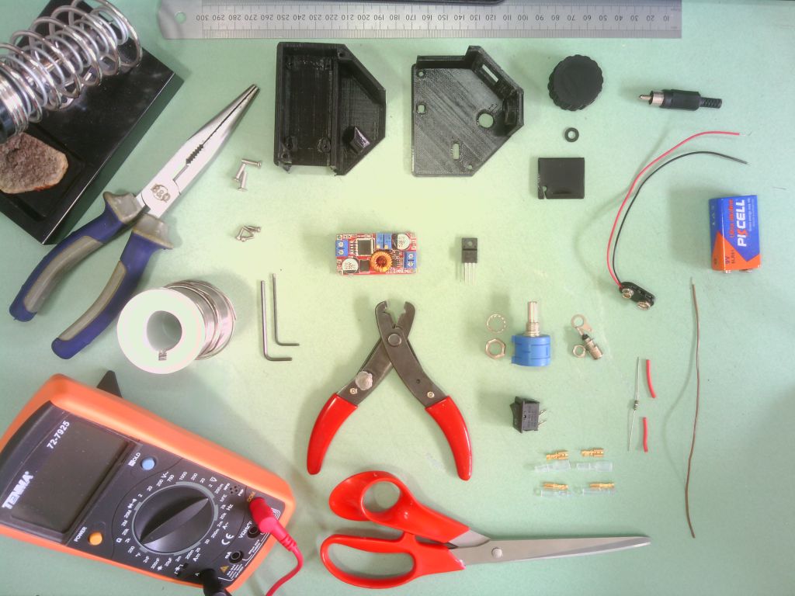
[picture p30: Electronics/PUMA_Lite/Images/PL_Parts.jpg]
Required Components

* The following 3D printed parts as specified in the 'PUMA_3D_Printing_Guide':
    > All parts in the chapter 'PUMA Lite'
* The following pre-assembled PCBs:
    > XL4015-based DC-DC step-down buck converter module with both current and voltage regulation of the type shown in the below picture.
    
    PUMA Buck converter
* Solder
* Phono socket panel mount type (and a phono plug to assist fitting the socket).
* P-Channel MOSFET, 78 A, 60 V, 3-Pin TO-220F ON Semiconductor BMS3003-1E
* Through hole resistor: 5 Ohm, 1%, 1W, Axial
* Precision potentiometer 200 ohm: Wire wound, bushing mount, Bourns 3590s type.
* ON/Off rectangular rocker switch, 10A/125V or 6A/250V, SPST type. Dimensions: Flange (2.05 cm x 1.5 cm), body size (1.8 cm x 1.15 cm) with 0.48 cm wide connector lugs. Switch body height below flange 1.05 cm and connector lug height 0.85 cm.
* One 9v PP3-type battery snap connector with 150 mm long leads.
* A power supply: Either a 9v battery (type 6LR61 PP3) or a mains regulated power adapter that can put out 9 volts regulated DC (actually anything between 8 V and 36 V will be acceptable) and at least 300 mA of current with a PP3 connector.
* Solderable spade connectors with insulator covers of sizes 4.8 mm and 2.8 mm (widths). You could forego these and solder all connections instead as an alternative. Particularly it may be advantageous to solder the leads to the potentiometer lugs as these are the ones most likely to fall off by accident.
* Scissors, screw driver, long nose pliars, some insulated wire and wire strippers

Additional Peripherals Required for Testing
-------------------------------------------
* A PUMA microscope LED lamp module

Fixtures and Fittings
---------------------
* All screws are of Allen socket type and made of stainless steel
* The case screws are countersunk. All other screws are socket cap screws.
* The number and type of screws used for each component are given below starting with the component they are to be used for. Lengths refer to the length of the threaded part of the screws (i.e. it does not include the head / socket).
* Case screws: 3x M3, 12 mm long
* Power board: 4x M2, 6 mm long

Tools
-----
* Wire cutters and wire strippers
* Long nose pliers
* Soldering iron, sponge, stand and fume extractor
* Allen keys (2 mm and 2.5 mm)
* Small Philips head screwdriver
* Multimeter with voltmeter and ammeter capabilities (to more than 1 amp tolerance)

Assembly Procedure
------------------
* Pre-thread all holes in the casing that are designed to take the thread of a screw. Don't go all the way in and be especially careful of the shallow holes on the front panel otherwise you could deform the external surface or go all the way through with the screw.
* Bend the pins of the p-MOSFET as shown in the figure. The middle pin is bent right back and the other two pins are bent and turned to line up so that they fit into the input terminal block of the buck converter as shown. The negative pin will need to be cut short by a few mm to allow this.

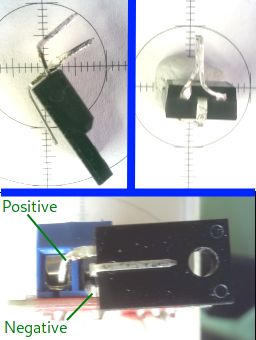
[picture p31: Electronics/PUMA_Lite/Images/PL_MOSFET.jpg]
p-MOSFET


* Take the PP3 connector and wrap the negative lead end around the negative pin of the p-MOSFET as shown in the figure (no need to solder it to the pin). To the positive lead of the PP3 connector solder a 4.8 mm spade connector. To the middle pin of the p-MOSFET solder a wire that has a 4.8 mm connector at its other end. You can then insert the p-MOSFET into the buck converter input block and connect the spades to the on/off switch. Finally, connect the 9V battery to the PP3 connector. The buck converter can now be powered up by turning the switch on.
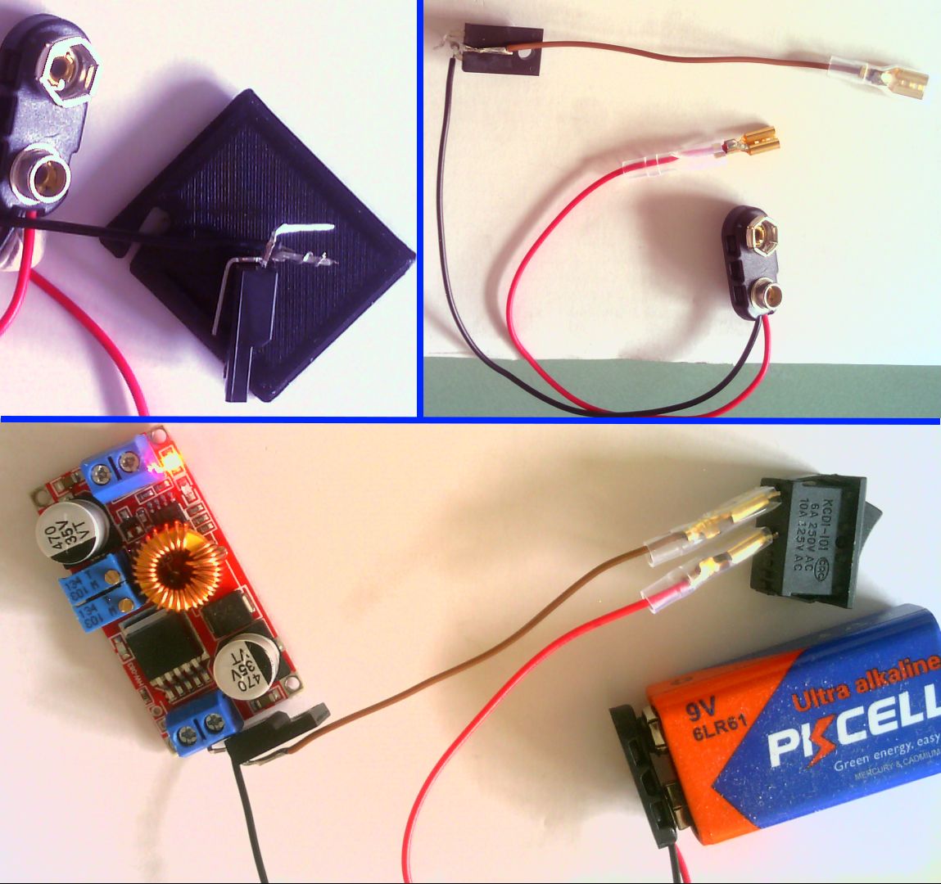
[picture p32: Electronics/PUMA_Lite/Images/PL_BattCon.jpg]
Battery connections


* At this stage,with the buck converter powered on, you should adjust the trimmer potentiometers on the buck converter to ensure the correct current and voltage regulations are set (see figures below).
* To set the correct current set your multimeter to measure current in the range of 20 Amps DC, place the meter probes on the output terminals and adjust the trimmer potentiometer closest to the output side of the board until a reading of 0.33 A is achieved. Note that the LED nearest the battery input terminals must be lit during this procedure to indicate that the board is limiting the current (as shown in the picture). If it is not lit, disconned and reconnect the power (using the on/off switch) and try again.
Set the current

* To set the correct voltage set your multimeter to measure volts (20 V DC range), place the meter probes on the output terminals and adjust the trimmer potentiometer closest to the input side of the board until a reading of 5.0 V is achieved. The buck converter board can now be powered down and the on/off switch disconnected from the spades.
Set the voltage

* Now create the three cables you will need to connect the output side of the buck converter board to the lamp brightness potentiometer and output phono socket (see picture). The shortest cable (~ 5cm) has a 4.8 mm spade at one end and a 2.8 mm spade at the other - it will be used to connect the brightness potentiometer to the phono socket centre terminal (positive). The second cable has a 4.8 mm spade at one end and a bare end - this connects the negative terminal of the buck converter directly to the negative / ground terminal of the phono socket. The third cable is made of the 5 Ohm resistor and a piece of wire with a 2.8 mm spade at the end of the wire and the other end of the resistor is just bent into a small loop - the looped end of the resistor will fit into the positive output terminal of the buck converter and the spade end will eventually go to the potentiometer.  
Output cables

Power outputs

* The buck converter can now be secured in the main body of the casing with the 4 M2 screws as shown.
Power board in place

* Now prepare the front cover part of the casing by inserting the connectors as shown in the below figure starting with the potentiometer, then the phono socket (having a phono plug inserted into the socket while fitting it will ensure good clearance of the socket from the walls of its receptacle) and finally the on/off switch is pushed into its rectangular hole with the bent spades pointing towards the top cover as shown. The small connector cable can then be used to connect the end connector of the potentiometer to the central connection of the phono plug - note that the small 3D printed plastic washer goes over the central lug of the phono socket prior to connecting the spade connector of this connecting cable (parts C and D of the fingure below).
Controls in place 

* Connect the output cables from the buck converter to the phono socket and central lug of the rheostat as shown in the figure below.
Power output cables to controls 

* Now connect the spades to the on/off switch and ensure that the battery connector leads are fit into the notch in the side wall of the casing as shown in the figure below.
Connect the on/off switch 

* Now fit the cover to the main casing, attach a battery, put the battery into the battery compartment and close that compartment with its cover. Put the knob on the shaft of the potentiometer. These steps are illustrated below. Take care to ensure spade connectors don't come loose. You may need to crimp them with the long nosed pliars. Take care also that the battery connector leads remain in the slot in the casing.
Close the cover 

* The unit is now ready for testing. At first just switch it on without any lamp attached (below figure, insert). The red LED should come on - if it doesn't you will need to double check all connections and components. If the red LED comes on then switch off, attach a PUMA lamp and switch on again  - turn the potentiometer to ensure brightness can be varied. On the latter point note two things:
1. The resistance is increased as you rotate the knob clockwise which means that brightness of the lamp will increased with anti-clockwise rotation and decrease with clockwise rotation.
2. The potentiometer is linear - for many turns you will not notice much change in brightness but there will be anoticeable increase in brighntess for the last few turns anti-clockwise.
Testing 

Tripping the Lamp Power Regulator
---------------------------------
* With the PUMA Lite, tripping the power regulator (as described for the PUMA Control Console) does not appear to be a problem in practice but we use the same fixed 5 Ohm resistor in the circuit for added safety and to make the illumination circuit with the PUMA Lite identical to the illumination circuit with the PUMA Control Console.

Power Consumption
-----------------
The PUMA Lite has no in-built ammeter. However measurements have shown that the output current to the lamp varies from about 10 mA at minimum brightness to about 290 mA at maximum brightness. The holes in the top of the casing allow visualisation of the LED indicators on the power regulator board.
When power is supplied to the power regulator board the LED closest to the output terminals of the power regulator board will be lit. This LED alone will continue to show when the bulb draws current up to about 27 mA. Higher current draw than that will start to illuminate the LED next to it (this just starts to come on at about 28 mA) and when both LEDs are at equal brightness the current draw is about 30 mA. The LED closest to the output terminals of the power regulator board will gradually weaken and switch off when the current draw to the lamp reaches about 32 mA. No change in LED status will be seen as the brightness is further increased but the maximum brightness occurs at a current draw of about 290 mA.
The LED on the other side of the power board will only go on if the current draw reaches 330 mA so this LED would not normally light at any stage.
From a 9 Volt battery the unit will consume about 1650 mW at maximum brightness and only about 185 mW at minimum brightness. The current drawn from the battery will vary between 260 mA and 25 mA respectively. If using a 12V external power supply the current draw will be between 167 and 22 mA.

PJT

First written: 07.06.2021

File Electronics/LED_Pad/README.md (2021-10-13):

PUMA Project: LED Pad Specifications and How To Guide
=====================================================

This project is released under the following licenses:

For source code (including CAD files, STL files and computer programs) and compiled code: the GNU GENERAL PUBLIC LICENSE Version 3

For documentation: the GNU Free Documentation License, Version 1.3

Introduction
------------
The LED Pad is a simple custom electronics connector board that allows a surface mount LED of the type used in the PUMA microscope to connect to the cable that brings it power. This board also allows that LED to connect by simple surface pressure alone - no soldering of the LED connector tags are required - so if an LED 'blows' or you want to switch to a different LED (e.g. switch between white light and fluorescein stimulating blue light) you can easily do this without soldering.
The LED Pad is made from standard tripad electronics prototyping board that is cut to size  - no PCB printing or etching or drilling is required.

Required Components
-------------------
* Tripad electronics prototyping board
* Aluminium sticky-back foil (or similar, e.g. copper tape)
* Thermal transfer paste
* Solder
* Track connecting wire: Single core wire that can be soldered and that can fit in the prototyping board's holes.
* Insulated power cable  50 cm long. Two connecting wires in this cable (one for positive and one for ground). There is no need for it to be coaxial or shielded. Speaker figure of 8 cable can be used (outer dims ~2.2x4.4 mm, inner core 8 strand copper conductor).
* Phono plug
* Electrical insulation tape.
* Suitable source LED. Dimensions diagram shown below. These are surface mount 1W COB LEDs with 8 mm diameter round ceramic body and polycarbonate dome. The round body has flattened sides to 7.26 mm and a 6 mm flat heat conducting base pad. Either daylight/pure white or 460nm blue types are used (for standard illumination and fluorescein fluorescence illumination respectively):
	White: Dominant wavelength colour temperature range is 6500-7000K. Voltage range 3.2 to 3.4 V. Brightness rating 100-110 lumens.
	Blue:   Dominant wavelength range is 460-465 nm. Voltage 3.2-3.6 V. Brightness rating 15-25 lumens.
Many other colours / wavelengths are also available for difference case uses and fluoreophores

PUMA LED Specs

Tools
-----
* Wire cutters and wire strippers
* Long nose pliars
* Soldering iron, sponge, stand and fume extractor
* Tools to cut tripad board to size
* Scissors, ruler and pencil.
* About a 3 cm length of 1.75 mm PLA filament (or some similar implement that will be used to apply heatsink paste to surfaces).

Procedure
---------
* Solder / connect the phono plug to one end of the power cable and strip the opposite bare ends by 2 mm or so and tin them.

* Cut a rectangular piece of tripad board consisting in 3 tripads down by 8 strips across (see picture below). The final size will be about 20 x 22.5 mm. File or sand down the edges so that the board will fit well into the recess in the 3D ptinted LED cover without being overly tight (part: DI_LED_Cover.stl).

PUMA LED Tripad Connections

* On the copper side of the board tin the tripads in the middle row which are 1 strip in from the edge stips (as shown in the figure) and from the non-copper side cut and solder the single core wire such as to connect those two tinned tripads to the tripads below them which are each one strip further towards the centre (as shown).

* Connect the power cable tinned ends to the two holes of the lower tripds closest to the lowest edge of the board as shown in the figure below. The pictures indicate polarity - the wire with the white stripe is connected to the central pole of the phono plug. Ensure this polarity is preserved.

PUMA LED Tripad Polarity

* Ensure no wires protrude from either side of the board. If the tinned middle row tripads are uneven in terms of the thickness of tinning solder then file or sand them down to be level with each other and no more than 1 mm in thickness of the tinning solder (preferably less than 1 mm).

* Cut a square of electrical insulation tape and apply it over the wires on the non-copper side of the board so as to avoid these being cross-circuited by the subsequent application of the heatsink conducter.

PUMA LED Tripad Insulation

* Make the heatsink conducter pad from a 24 x 34 mm piece of the self-adhesive foil as shown in the pictures below (all measurements are in mm).

PUMA LED Tripad Heatsink

* Apply the heatsink conducter pad as shown below taking care not to cross circuit the two central tinned tripads to each other.

PUMA LED Tripad Heatsink

* When ready to fit the board to the LED holder and LED apply heat transfer compound to the heatsink area of the LED and board using your applicator before attaching the board to the LED.

PJT

First written: 01.03.2021
Last edit: 13.10.2021

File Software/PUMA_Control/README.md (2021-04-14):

PUMA Control
============

Introduction
------------
The 'PUMA_Control' software is a package for Arduino Nano that serves the PUMA Control Console (PCC) including the heads-up display (HUD) of the microscope and some basic aperture generation tools for the spatial light modulator (SLM). This includes interactive measurement functions, a timer, a pointer, various graticule overlays, Z-motor control, a real-time lamp current meter and other facilities.

Special Libraries
-----------------
This program uses a modified version of the Adafruit GFX library where the default font has been customised to draw mirror writing and also to draw custom graphics characters. I place this custom version into a copy of that library called GFXM (in the libraries folder GFXM_Library) so that this does not get overwritten each time the standard Adafruit graphics library is updated). This also includes its own version of the standard Arduino library Print.cpp file which ensures writing is right to left - i.e. mirrored.
This also uses a slightly modified version of  Pawel A. Hernik's "Arduino_ST7789_Fast" library which I made called 'ST7789_FastM'

How to Use
----------
This is only a brief quick start guide. See the full [PUMA Control_User_Manual](../PUMA_Control_Manual.pdf) for detailed and illustrated usage information.
Once loaded onto the Arduino Nano the Nano should be connected to the peripherals of the PUMA Control Console as described in the 'How To' guides for making that console. The following assumes all is working correctly - both hardware and software.
Turn on the console power switch.

Boot Up Screen
--------------
After a few seconds a double beep occurs and the boot up screen appears to let you know the program is ready to use.
In the boot up screen you have 3 options:
1. Press the left button to initiate a Z-Homing procedure (the Z-stage motor must be homed before you can use it but you are free to use the rest of the software function without homing the motor - e.g. if you do not have a motorised stage or if you just want to use manual focus)
2. Press the right button to take you to the main menu to select a control mode
3. Press the central joystick button to mute the device (you will hear a trill indicating that the device has gone into mute). Press the central joystick button again to undo mute (there will be no audible signal for this).

Main Menu
---------
The main menu is entered by a press of the right button. You go back one menu level or exit the menu also by a press of this button.
The joystick buttons allow you to navigate the menus

Control Modes
-------------
The 'control modes' are the main working modes outside the menu and you select which control mode you want to work in via the menu. When in the control modes you can use the joystick and the two buttons on the control pad either individually or in combinations. These are the available control modes and a brief description of what they allow you to do:
1. Z-Motor: Home the Z-stage via its motor and limit switch. Control the focus of the scope. There is a quick shortcut that allows you to go into and out of Z-motor control mode from almost any other control mode and that is to simultaneously press the left and right buttons (but you must press the left button first briefly). This allows you to control the focus of the scope motor while working in other control modes.
2. Pointer: Control an interactive pointer on the HUD which can be used for pointing, marking objects, counting objects and drawing lines to be measured in length and angle.
3. Timer: Set and use a count-up or count-down timer. The time will continue to count time even when you move to a different control mode so it can be used simultaneously with other modes.
4. Graticule: This allows you to superimpose a range of graticules on the field of view via the HUD. Each graticule can be varied in scale and colour.
5. Plain: This sets a completely plain field of view on the HUD which can be varied in colour. Use this for illumination effects. When used with the SLM this can act as a programmable colour filter to colour the illumination of the scope.
6. Aperture: This allows apertures of various sizes to be generated for use with the SLM. You can cycle between a plain bright field circular aperture (open and close it in graded steps), a half-field Schlieren aperture for phase contrast (you can rotate it by 90 degrees as desired) and a central stop aperture of various sizes for dark field microscopy. You can also superimpose the dark field central spot onto either of the two preceding patterns.

The Meaning of Audible Signals
------------------------------
The only source of visual feedback is the HUD or SLM display. If you do not use either of these devices then the PCC can still be used e.g. for control of the Z-motor and also it gives an audible warning if the LED bulb is being over-powered. You could always attach a free 5 volt ST7789 TFT module to the unit to get visual feedback of the GUI if you like ('free' as in not part of any module) but you would need a mirror to read it! If you don't want to do that then the audible signals have been carefully designed to have meanings that will help you know what you are doing. These are the audible signals and what they mean:

// Buzzer Signals  
#define BZ_SILENCE      0  
#define BZ_ACKNOWLEDGED 1  
#define BZ_PROMPT       2  
#define BZ_FORBIDDEN    3  
#define BZ_TRILL        4  
#define BZ_LAMPHOT      5  
#define BZ_TIMEOUT      6  

**SILENCE**  
A special case override to the ACKNOWLEDGED signal for certain key actions. Specifically when moving the pointer around or moving focus up or down then the ACKNOWLEDGED signal is replaced by SILENCE (i.e. no sound and no delay in the navi_loop function that looks for key actions).

**ACKNOWLEDGED**  
Single beep = acknowledge a key action. The total amount of delay introduced by a buzzer signal must be at least 200 ms regardless of Acklen in order to minimise the risk of inadvertent double-key activation.

**PROMPT**  
Double beep = bring user's attention to a normal state or decision. For example when boot up is complete (so the system is ready to accept key commands) or when a confirmation question requiring a response is being asked by the system ('Do you really want to delete all data points?')

**FORBIDDEN**  
Triple fast beep = bring user's attention to an inability to perform the desired action (due, e.g. to a limit having been reached or a condition not met). This will occur if a user tries to access motor functions if the motor has not been homed or a min/max motion limit is reached. It will also sound if you try to undo a drawing mark when there are no more marks left to undo, etc.

**TRILL**  
Trill = The system is entering silent mode. This is essentially a very fast triple beep. This is the only meaning for this signal.

**TIMEOUT**
6 beeps = the end of countdown audible signal for the timer. This will override the mute setting if the user has set an audible signal for a count-down (either alone or in combination with a visible signal).

**LAMPHOT**  
4 beeps  = the lamp is being over-driven with too much current and may be destroyed if immediate action is not taken. This will override the user's mute preference because it is a safety warning.

Notes:  
Sometimes a PROMPT or FORBIDDEN signal will be immediately followed by the single beep of ACKNOWLEDGED, at other times it won't.

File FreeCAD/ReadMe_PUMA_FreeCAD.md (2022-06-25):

PUMA CAD Files
==============

Introduction
------------
These are the source CAD files for the PUMA 3D-Printable Microscope Project. Note that you will need other components in addition to the 3D printed parts represented here to build the modules. For example, screws and lenses. Details are given the the construction documentation and YouTube videos.

These CAD files were made in FreeCAD v. 0.19 using 64 bit Arch Linux. **I also use the Fasteners Workbench add-on for FreeCAD which you may need to properly view some files.** You can install the Fasteners Workbench by following the instructions given here: https://wiki.freecadweb.org/Fasteners_Workbench

For information on how to generate STL files from the models in these CAD files, see the 'PUMA_3D_Printing_Guide' in the 3D_Printing folder on the PUMA GitHub page.

Updates to models that have occurred since the v1.0 release are described in the YouTube videos and some are also described in detail below. Many models have been updated since the v1.0 release so please use the models from the current main branch of this GitHub repository when building any part of PUMA.

At the end of this document therr is a summary of what each file contains is given below. For details about the parts and construction of the microscope see the detailed documentation and tutorials.

Updates to the Abbe Condenser Module
------------------------------------
Since making the video on the Abbe condenser it has come to my attention that there are at least 3 variations of 30 mm lens that are sold by different suppliers (shown in the photos below), not all of which are acceptable for use in the condenser module.

30mm lens variants

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

Summary of Each File
--------------------

**AR_Projector**

 The augmented reality projector used to provide a heads-up-display.
 
**Binocular_v3.1**

 Parts required for the binocular head module of the microscope. Only parts specific to the binocular attachment are in this file. The binocular head module also uses some parts that are common to the monocular head attachment which are not duplicated here - see the file 'Monocular_v1.1' for those common parts.
 
**Dominus_v3**

 The Dominus Illumination System. This includes the parts required for the various illumination options and modules of the microscope.
 
**FilterBlock_v2.1**

 These are the parts for that segment of the optical tube of the microscope that goes between the objective quick release receptacle and the ocular head module. It includes two options - a simple filterblock and an advanced filterblock. The simple one has space for two slider filters only. The advanced module has space for 3 slider filters, an optional infinity optics tube lens and a beam splitter / beam joiner cube to allow for epi-illumination, fluorescence, and use of the AR projector.
 
**Focus_Gears**

 The parts needed to make and assemble the geared timing-belt driven Z-stage focus mechanism. Any parts specific to the motorisation option are found in the 'Z_Motor' file, not here.
 
**Legs**

 The various legs used to support the scope in its various configurations.
 
**Monocular_v1.1**

 Parts for the monocular head. This includes ocular mounting parts that are common to all ocular configurations - monocular, binocular and trinocular.
 
**PUMA_Control**

 Parts for the main PUMA Control Console.
 
**PUMALite**

 Parts for the simpler PUMA Lite console
 
**QuickRelease_v2.0**

 The objective holder which joins to the main optical tube.
 
**Stage**

 The main XYZ stage parts. Use this in conjunction with the 'Focus_Gears' to build a complete PUMA microscope stage mechanuism. This can be motorised in Z using the parts from the 'Z_Motor' file (with motor driven by the PUMA Control Console)
 
**Trinocular_CP_v1**

 The Trinocular / Camera Port tube. This connects to the epi-illumination port of the advanced filterblock to provide an outlet for a third ocular port. This file only contains the tube that connects the parts because the remaining parts are found in other CAD files. For example the 90 degree ocular lens holder is found in the Binocular CAD file. Details of what parts are needed and where to find them are given in the detailed construction documentation.
  
**XY_Stabiliser**

 This is an optional add-on that makes the XY slide mechanical calipers more stable i.e. less prone to wobble and lift. It is not always necessary.

**Z_Motor**

 These are the components required to connect a motor to the microscope stage for motorised focus / Z-motion.

PJT 25.02.2021

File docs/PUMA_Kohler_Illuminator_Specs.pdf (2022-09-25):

# PUMA Köhler Illuminator

## PUMA: The Open Source (GPL v3.0) 3D printed microscope system designed for direct eye


### Specs and Supplementary Information

Document created: 28.11.2021, Last edited: 25.09.2022

observations and ultra-portability with advanced options for digital imaging, measurements and computer control.

Contents

[This space is intentionally left blank]

PUMA Köhler Illuminator Supplementary Doc v1.0 | Page 2

### Legal Information

License

Copyright (C) 2021−2022 Dr Paul J. Tadrous

Permission is granted to copy, distribute and/or modify this document under the terms of the GNU Free Documentation License, Version 1.3 or any later version published by the Free Software Foundation; with no Invariant Sections, no Front-Cover Texts, and no Back-Cover Texts. A copy of the license can be found at https://www.gnu.org/licenses/fdl-1.3.html

Limitations of Use The PUMA microscope and its associated systems do not have any certifications or regulatory approvals in any country for use in clinical diagnostics or treatment (human or veterinary). The PUMA microscope and its associated systems are released to be used for research and educational purposes only.

Disclaimer All PUMA project information, including without limitation any CAD file or STL file and all documentation, advice and instruction (whether provided in video form, audible form,

written form or otherwise) is provided ‘as is’ in good faith and is intended to be helpful but comes with no warranty whatsoever. Anyone attempting to build or use a PUMA microscope or other PUMA-related material, accessory, module or derivative is hereby advised that there will be risk involved in 3D printing, post-print processing, assembly and usage of the resulting structures. This risk includes, without limitation, the risk of personal damage and loss of resources.

Dr Paul J. Tadrous, TadPath and OptArc cannot accept any liability for any such loss or damages that may occur. All those who attempt to build or use any aspect of the PUMA project or derivatives thereof do so at their own risk.

### Safety Information

Throughout this manual please take heed of warnings given in bold text and highlighted yellow to avoid possible damage to equipment and/or harm to people.

PUMA microscopes and associated systems are not toys. They contain small parts which may come loose such as tiny metal screws and washers and glass components that may splinter or break or otherwise present a choking or sharp object hazard or chemical hazard (for batteries). Please do not let babies or young children play with or use any aspect of a PUMA system without close appropriate adult supervision. Likewise keep PUMA systems away from pets.

### Abbreviations

Some common abbreviations used in this documentation

KI = Köhler illumination

NA = Numerical Aperture

BFP = Back Focal Plane

CFP = the condenser’s lower (front) focal plane IAD = Illuminating Aperture Diaphragm of the condenser IFD = Illuminated Field Diaphragm (Field stop, Köhler diaphragm) LPC = low power collector

LC = 2x23 mm lower collector

### 0. Introduction

The PUMA Köhler Illuminator is described in detail in this YouTube video:

https://youtu.be/XEE-el7vC5k

This document gives some supplementary information and specs to assist in deciding the best usage for your project.

Here I also show results and calculations for the maximum NA of the PUMA condenser system with and without the Köhler illuminator.

This document is under constant revision and should not be considered complete and final.

### 1. Lens and Optical Path Specifications

Figure 1.1 shows the optical train of the Köhler-Abbe system with the standard 2x23LC (no spacer and no LPC). Refer to the figure legend for more detail about lens spacing.

Figure 1.1. Arrangement of lenses and
measurements for the Dominus Köhler
illuminator | using | the | 23/30 | Abbe
condenser. Cnd = condenser, the lenses being arranged at a distance apart that just allows an object placed at the flat surface of the 30 mm lens to appear in focus when looking into the distance from the top of the 23 mm lens (position of observer marked with eye symbol). The back surface of the 30 mm lens is therefore, by definition, the back focal plane (BFP) of the condenser assembly.

IAD = illuminating aperture diaphragm. This is placed at the BFP of the condenser. UC = upper collector. This is positioned at such a distance (labelled as 'x' mm) from the condenser so that if an observer looks through the 23 mm lens of the condenser they will see objects at infinity in focus – the condenser/UC assembly therefore will

form a telescope focussed at infinity from the point of view of the observer when x is appropriate (in practice x is about 23 mm). This implies that the front focal plane of the UC lens coincides with the BFP of the condenser. IFD = illuminated field diaphragm. This is placed at such a distance from the UC and condenser combination that an image of the IFD is

brought to a focus at the level of the specimen on the slide. In this figure the distance from the lamp housing is shown (20 mm) and this translates to 96-20 = 76 mm from the lowest point of the UC 44 mm lens. LC = lower collector lens assembly and is made from 2 closely applied 23 mm lenses (they are about 8.25 mm apart, held that way by the 7 mm collar). The LC is designed to produce a collimated parallel beam of the light emitted from the LED source. However, all the lenses used

in this Kohler system are not perfect and some adjustment of the distance of the LC from the LED is required for optimal illumination of the x40 lens compared to all the lower powered objectives. The distance shown as 'y' represents this adjustment. The figure illustrated the extended lampholder container and y is measured from the lip of that lampholder to the lip of the LC housing. When the LC is fully lowered the back of the second lens just touches the plastic dome case of the LED and y=3.5 mm. This is the position used for all except the x40 objective. For the x40 objective the LC assembly is brought forward (moved away from the LED) by 1.5 mm so y = 5 mm. The whole length of this Kohler illuminator is 171 mm from the bottom of the stage to the bottom of the lamp housing.

Table 1.1 gives the specifications of the lenses used in the Köhler illuminator and Abbe condenser (measurements are in mm). The symbols in the table refer to the measurements shown in the figure 1.3 and three focal lengths are provided for each lens. The ‘nominal’ focal length is the focal length specified in the seller’s / manufacturer’s web page. The other two focal lengths given are actual measurements made (by me) with a parallel collimated laser beam expanded to 5 mm in diameter approaching the lens from the side shown by the two parallel arrows as shown in figure 1.4.

Lens ID | Uses | D | L | Dc | Te | Tc | B | P | f nomin al | fB | fP
44 mm | Köhler | 44 | 2 | 40 | 3 | 19 | 16 | 0 | 23.00 | 49.00 | 24.00
30 mm | Abbe Cnd | 30 | 1 | 28 | 3 | 15 | 12 | 0 | 25.00 | 31.50 | 10.50
30 sq.parab | Alternative Abbe | 30 | 2 | 26 | 2.5 | 13 | 10.5 | 0 | | 34.80 | 13.90
30 sq. sph | Not used | 30 | 1 | 28 | 3 | 10 | 7 | 0 | | 40.00 | 28.60
23 mm | LC, Abbe Cnd | 23 | 1 | 21 | 1.25 | 8 | 6.5 | 0.25 | 18.00 | 28.00 | 17.70
LPC Lens | LPC | 23 | 0 | 23 | 2 | 4 | 2 | 0 | 60.00 | 61.00 | 56.20

Table 1.1 Lens parameters for the Köhler illuminator and Abbe condenser (all measurements in mm). For meaning of symbols see figure 1.3 and main text. There are three 30 mm lenses in the table. The first is the original 30 mm lens used in this project. This lens may not be available from all suppliers so two alternatives are shown. The ‘sq. parab’ is a paraboloid shape lens with a squared off rim. This is slightly ‘weaker’ (i.e. has longer focal lengths) than the original. The second alternative ‘30 sq. sph’ is much weaker and should not be used (details are given here so you know if you receive one of these lenses from a supplier). Figure 1.2 shows photos of these three lenses so you can see the difference between them in shape. The ‘LPC Lens’ is the thin lens used in the LPC attachment.


Figure 1.2. The three different types of 30 mm lens you may receive from online sellers. Only the two on the left may be used for making a PUMA Abbe condenser. If you get the spherical type (shown on the right) this will be too weak to give a high numerical aperture fan beam and appropriate access to the Fourier plane so should not be used.


Figure 1.3 Lens dimensions. The symbols are those used in table 1.1.

Figure 1.4. Definition of the two focal lengths measured for the figures in table 1.1. Arrows on the left indicate the incident collimated beam expanded laser beam. Vertical line on the right indicates the plane this beam

comes to a focus in. Figure 1.5 shows the optical path through the system.


Figure 1.5. Light path from a point on the LED source for the Dominus Köhler illuminator using the 23/30 Abbe condenser.

The slightly longer focal lengths associated with the new form paraboloid 30 mm lens may be expected to give slightly lower NA illumination to the original and may also slightly offset the Fourier plane, in theory. However practical experiments have since shown that neither of the above two expectations are realised in practice – at least not in a simple way. Regarding access to the Fourier plane, this is maintained with the new form paraboloid 30 mm lens. Because these lenses are not planatic the whole Fourier plane is not in

focus all across the field (with either the original or the new 30 mm lens). The new form 30 mm lens has better focus near the central area of the Fourier plane and the original 30 mm lens has slightly better focus near the periphery of the Fourier plane. However these differences do not make one lens overall better than the other and the Fourier plane is essentially in correct focus with both lenses taking the lack of planarity into account. For the effects on NA of illumination see table 4.1 and the discussion in section 4 below.

### 2. System Configuration Options

One of the key features of KI is the use of a collector system to project an image of the light source into the front focal plane of the condenser (its ‘lower’ focal plane in the upright configuration – also known as the Fourier plane and it is a conjugate focal plane of the back focal plane, the BFP, of the objective lens).

The ideal condition – for standard bright field viewing − exists when the condenser’s focal plane (CFP) is filled with a uniform patch of light up to the maximum numerical aperture (NA) of the objective lens in use.

Due to the limitations of the lenses used, there is a trade off between the size of the uniform area of illumination at the specimen plane and the NA of the fanned out beam produced by the condenser. The former is needed to completely illuminate the field of view and the latter is needed to make maximum use of the objectives resolving abilities. It is often the case that these two features are inversely related – the greater the NA the smaller is the illuminated field patch and vice versa. This relationship is not catastrophic however because higher NA is needed for higher magnification lenses which also have a small field of view. It does mean, however, that configurations which give the highest NA of illumination will not fill the field of view of lower magnification lenses and so there are some optional configurations of the lens system for the PUMA KI system that maximise / optimise viewing for either low magnification or high magnification lenses. These options include the number, type and spacing of lenses of the lower collector and Abbe condenser and whether or not to use the 5 mm spacer and / or a diffuser in the LED lamp housing.

Consequently I have made measurements on the size and distribution of the patch of light produced by the PUMA KI system in the CFP and the NA of this projection so as to assess which configurations will work best for various objectives and uses. This guide documents those measurements.

### 2.1 Condenser Focal Plane Projections

With the the empty (lensless) Abbe condenser in place, the size and distribution of light projected on the CFP was measured by inserting a sheet of drafting paper (tracing paper) into the IAD slot to act as a back-projection screen and photographing the resulting projections from directly above. Figure 2.1.1 shows the lensless condenser with the drafting paper inserted. These measurements were made for all the configurations of the lower collector specified below.


Figure 2.1.1. A back-projection screen is inserted into the IAD slot of the lensless condenser to make measurements of the light projected there by the collector system of the Köhler illuminator. 2.2 Numerical Aperture Measurements by the Horsfall Method With the full Abbe condenser in place and no restrictions on either the IAD or the IFD, an

Olympus SPlan x40 objective was used with a blank slide in place on the stage (the scope was first focussed on a specimen slide then the specimen was removed and the blank slide inserted). See figure 2.2.1. The eyepiece was removed from the optical tube and the camera looked directly down the optical tube and was focussed on the BFP of the objective. Images were taken for all the configurations of the lower collector specified below. The Olympus x40 objective has a stated NA of 0.7. To get a control image of the full NA of

illumination I used an identical setup but with the KI system and Abbe condenser removed and with a sheet of paper placed on the stage, extensive enough to more than exceed the NA of the objective. This paper was illuminated from below by a desk lamp and the standard mirror illuminator (see figure 2.2.2). For experiments with even higher NA objectives (0.95 and 1.25) the optical tube with objective in place was removed from the scope and placed up close to a a flat expanse of light that was sufficient to fill the NA of the lens.


Figure 2.2.1. Stage and objective setup for measuring the NA of the illumination system with an Olympus SPlan x40 objective of stated NA = 0.7.

Figure 2.2.2. Setup for measuring the full NA of the objective for a comparison control. A desk lamp fluorescent strip is placed on its side and the mirror reflects the extensive light up to illuminate a piece of paper on the stage (without any condenser present). The view from the top is seen with the camera iris open

(middle) to show that the camera is looking directly down the optical axis. The camera iris is stoppered down to f = 4.0 to remove saturation and make all the subsequent measurements (right).

### 2.3 Lower Collector Configurations

The following variations of the lower collector were used for make all measurements. In addition, for each configuration the measurement was made with and without the 5 mm spacer between the LED and the first collector lens and also with and without a membrane diffuser behind the first collector lens.

A. The LPC without a proximal lens. B. The LPC with one proximal lens (this is the usual way to deploy the LPC) C. The LPC with two proximal lenses. This is the ‘usual’ LPC but with the single proximal lens replaced by the 2x23 mm lower collector (LC) D. The LC on its own

The configuration letters A to D above are illustrated in figure 4. Configuration C does not give full KI because the projection is shifted slightly towards critical illumination and it is no use for low power objectives. However it can give useful flat field illumination for higher magnification objectives e.g. x10 and above so is convenient if you want to use the LPC setup for x4, you can leave the LPC tube in the IFD tray and

simply swap out the proximal lens for the LC to view higher magnifications. This is useful also because precise alignment of the lamp may differ between using the LPC and the LC when each is directly coupled to the IFD via the same adjust ring.

### 3. Results: Condenser Plane Projections

Figures 3.1 and 3.2 show the condenser plane projections. The camera was kept at constant manual settings for all measurements so the brightness can be compared between configurations.

A membrane ND filter was used for all measurements. When a diffuser is inserted this is always inserted in front of the ND filter.

The camera used is a Panasonic HC-X800 3-chip camcorder on manual mode with iris set to 4=4.0 and shutter set to 1/4000.

Each square in the matrix shown in figures 3.1 and 3.2 have a physical size of 20 mm x 20 mm.


Figure 3.1. Results of condenser plane projection for the various configurations of the PUMA KI system. The capital letters down the side refer to the lower collector lens variant used as described in the text and also

illustrated in the diagrams far left. These images show the projections in a natural linear scale of intensities. The thin dark straight lines and occasional dark specs you see are simply folds and small defects in the drafting paper screen.


Figure 3.2. Condenser projections shown with intensity levels multiplied by 2 (left) and square root transformed (right) to make it easier to perceive the shape of the light distributions. The arrangement is the

same as described in figure 3.1. These results show that the light distribution varies in intensity in the CFP. From the perfect defocus principle this variation will not translate to the specimen plane but it does mean that resolution will vary accordingly. For the more even resolution spectrum a more uniform disc is required. The diffuser clearly helps in this regard.

Note that the smallest discs (and therefore the smallest NA of illumination) are made with the LPC lacking a proximal lens and the largest discs are made with the LC and the LPC using the LC as proximal lens. However, the LC used with the 5 mm spacer shows the largest discs by a small margin showing that for best resolution with a x40 objective and above you should use the LC with 5 mm spacer and a diffuser will give a more even spatial resolution spectral profile.

### 4. Results: Condenser NA Measurements

Figure 4.1 shows the control image of the full disc of illumination of the Olympus x40 lens representing a NA of 0.7

Figure 4.1. The full 0.7 NA of the x40 objective used in these tests. The image on the right shows a red ring drawn at the circumference for superimposing on the rest of the measurements to see how close they come to this ideal NA.

Figure 4.2 shows the results for the various illumination configurations used. The image matrices have the same meaning in terms of configurations as those used for condenser plane projection (see above). The camera shutter is 1/50 and the iris is set to f=4.0.


Figure 4.2 Illuminated numerical aperture of a x40 objective with full NA of 0.7 represented by the red rings. Left: Original linear intensity levels. Right) Square root transform of intensity levels. The meaning of the rows and columns are the same as for figures 3.1 and 3.2. The peripheral irregular thin crescents seen in images

B3 and B4 are due to the ND filter that was used not being large enough to cover the whole back surface of the first collector lens. It is interesting and important to note that, while the general shape of illuminated area is similar to the condenser plane projections as expected, the presence of an objective lens

increases the contrast and exaggerates the uneven distribution in intensity of the light across the field in this conjugate Fourier plane compared to where the images of the light source was first formed (the CFP). The implication being that use of the membrane diffuser is even more helpful in evening out the spatial frequency profile of the illumination than may at first have been thought looking at the condenser projections alone.

It is also clear from these results that in order to satisfactorily illuminate a high power objective such as x40 you will need to use either the LC or the LPC with LC as proximal lens.

However, the LC alone only illuminates about half the available NA unless the 5 mm spacer is used. In this case you get enhanced high and low spatial frequencies with a relative inter-band deficiency unless a diffuser is also used. Hence, best illumination for x40 and above will be with the LC using the 5 mm spacer and diffuser. The LPC with LC as proximal lens looks as though it will give reasonable illumination of a x40 objective with or without a spacer / diffuser. However, the extreme exaggeration of central low spatial frequencies as shown here tends to give a poor quality image in practice unless this profile is evened out with the use of a diffuser. In practice the image seems best without the spacer.

As the new form paraboloid 30 mm lens has a slightly longer focal length compared to the original paraboloid 30 mm lens it will refract light slightly less. This may be predicted to provide a slightly lower NA but the following experiments show this is not always the case. To examine what the differences are in practices, comparisons were made with the condenser using the original 30 mm lens and the new 30 mm lens. Results for dry objectives are shown in figure 4.3.


Figure 4.3 Comparison of the NA of the Abbe condenser made with the original 30 mm paraboloid lens (“Orig.”) and new paraboloid 30 mm lens (“New”). The left panel shows results with an Olympus SPlan x40 objective with NA = 0.7. The top row is with the Köhler illuminator (without a diffuser) and the bottom row without the Köhler illuminator (just using the condenser alone with diffuse illumination of its entire aperture using a method similar to that shown in figures 2.2.2 and 4.1). The right panel shows the full NA

of the diffusely lit condenser (no Köhler illuminator) with an Olympus MSPlan dry infinity corrected x100 objective with stated NA of 0.95 compared to the full NA of that same objective without a condenser. Both condensers have essentially the same maximum NA of just over 0.92 compared to this. More accurate quantitation of condenser NA is given in table 4.1 The results in figure 4.3 show that the NA of the condenser using the new 30 mm lens is essentially the same as when using the original 30 mm lens by visual inspection for these dry lenses. Both condensers fill the entire 0.7 NA of the Olympus x40 objective and both show essentially the same maximum NA (of just over 0.92) when compared to the full aperture of a 0.95 NA Olympus MSPlan x100 dry objective. For more detailed results I performed quantitation of the NA of the condenser (without the Köhler illuminator, i.e. using full illumination of the lower aperture of the condenser with an external diffuse light source – so not restricted to the limited size disc of light projected by the Köhler projector). The results are shown in table 4.1

Objective | Base parts | Condenser NA (original) | Condenser NA (new)
Dry x40 | On | 0.703 | 0.705
Dry x100 | On | 0.921 | 0.923
Dry x100 | Off | 0.925 | (not tested)
Oil x100 | On | 1.117 | 1.106
Oil x100 | Off | 1.126 | 1.143

Table 4.1. Numerical aperture measurements of the PUMA condenser using the Horsfall method. The objectives used were Olympus SPlan dry x40 (NA 0.7), Olympus MSPlan dry x100 (NA 0.95, infinity corrected objective), Zeiss Plan oil-immersion x100 (NA 1.25). The immersion oil used was Leica DIN immersion oil with NA=1.518 and was applied to both the condenser-slide interface and the coverslip-objective interface. ‘Base parts’ refer to whether the IAD slot and base of the condenser were in place (‘On’) or removed (‘Off’) for the measurement. Two condensers were tested, one with the original 30 mm lens (‘original’) and one with the new style 30 mm lens (‘new’).

Because the base two 3D printed components of the condenser assembly (that make up the IAD filter slot and connection thread to the mirror or Köhler illumination system) partially obscure the full aperture of the bottom aspect of the 30 mm lens to wide angle illumination, I tested the condenser with and without these base parts. The only real significant improvement seen without these parts comes with NA over 0.92 – i.e. using oil immersion for higher NA objectives.

Simplistic expectations that the new form factor 30 mm lens might give lower NA compared to the original 30 mm lens (that has slightly shorter focal lengths) were not born out by these experiments. It turns out that the ‘square base’ rim of the new form factor 30 mm lens can refract and internally reflect light at the periphery in such a way as to compensate (or even over-compensate) for its slightly longer focal lengths. This is responsible for the surprise result that the maximum possible condenser NA is actually higher (NA = 1.143) with the new form-factor lens than the original (NA = 1.126). Figure 4.4 shows the comparison between the illuminated apertures with the original and new 30 mm lenses in the oiled PUMA Abbe condenser compared to the full 1.25 NA aperture of the x100 oil lens.


Figure 4.4 Comparison of illuminated apertures in the back focal plane of a Zeiss Plan x100 oil immersion lens with full NA illuminated (centre) compared to illumination with an oiled PUMA Abbe condenser using the original 30 mm lens (left) and new form 30 mm lens (right). Note the slight improvement (increase) in NA with the new form factor lens. Although the PUMA condenser still cannot give full 1.25 illumination, the 1.143 illumination provided by the new form 30 mm lens gives a very useable illumination even with x100 oil immersion lenses provided that both the condenser and the lens are oiled. A small air bubble in the oil is seen bottom right in the left hand image. This does not affect the NA measurements.

In figure 4.4, the peripheral off-centre dark rim you see inside the light disc with the new 30 mm lens condenser is the junction of the flat rim of the 30 mm lens with its parabolic curved surface. The fact that this rim can also contribute to the illuminated disc is what pushes the NA of the new form factor lens just above that of the original lens, despite the fact that the focal length of the new form factor lens is slightly longer than the original (and so would lead to a simplistic prediction of lower NA illumination).

### 5. Some General Rules of Thumb

Empirical tests (backed up by the data gathered in the preceding measurements) have shown the following.

For a x2.5 and x2.0 objective you use the 2x23 mm LC with a spacer and a diffuser but use a hollow condenser.

For a X4 objective with the 2x23 mm LC this works best without spacer and without diffuser but lamp needs to be accurately centred. If using a spacer then a diffuser MUST be used (unless you are doing this for alignment purposes) and there is greater field curvature but the illumination is useable for direct vision (without a diffuser but with a spacer you get an image of the lamp – i.e. near critical illumination). For a X10 objective with the 2x23 mm LC this works best without spacer. For a X40 objective with the 2x23 mm LC this works best with spacer and if you use a diffuser you make the power spectrum more even (as illustrated above) so this is to be preferred but visually the difference is hard to notice with or without a diffuser.

We have seen that the LPC without a proximal 23 mm collector gives a lower NA projection cf. with a proximal lens – however this small projection still fills the back focal plane of the x4 lens so in theory and for normal bright field vision this does not matter and the illumination is uniform and good. However, I noticed that dark field microscopy seemed subjectively more even with a single 23 mm proximal lens compared to this lensless config. The LPC can be used with the 2x23mm collector without a spacer but with a diffuser to

give even illumination of x10 and x40. This usage is not true Köhler because the image of the LED source is not projected onto the lower focal plane of the condenser however it gives nice even illumination so that aspect of Köhler is not necessary (provided a diffuser and no spacer is used) and both diaphragms can still be used as with standard Köhler.

In general, when doing Fourier filtration at the CFP (for example, dark field microscopy) a diffuser should be used otherwise the yellow and blue/white colours of the projected image of the LED lamp will get ‘unmixed’ by the filter (such as the patch stop) and the images will have a partial ‘Rheinbergian’ look to them. For very high NA imaging, the disc of light produced by the Köhler illumination projector is insufficiently large to fill the lower focal plane of the condenser so alternative means of illuminating the condenser must be used for best (highest resolution) results. When used in this way the PUMA Abbe condenser can provide a maximum NA of 1.143 when used with DIN immersion oil between the condenser and the slide as well as between the coverslip and an oil-immersion objective and with the lower elements of the condenser

casing removed to allow maximum angle of incoming light to hit the bottom of the 30 mm lens.

### Work Still to Do

1. Experiments with the lensless condenser with an objective.

## [End of Document]

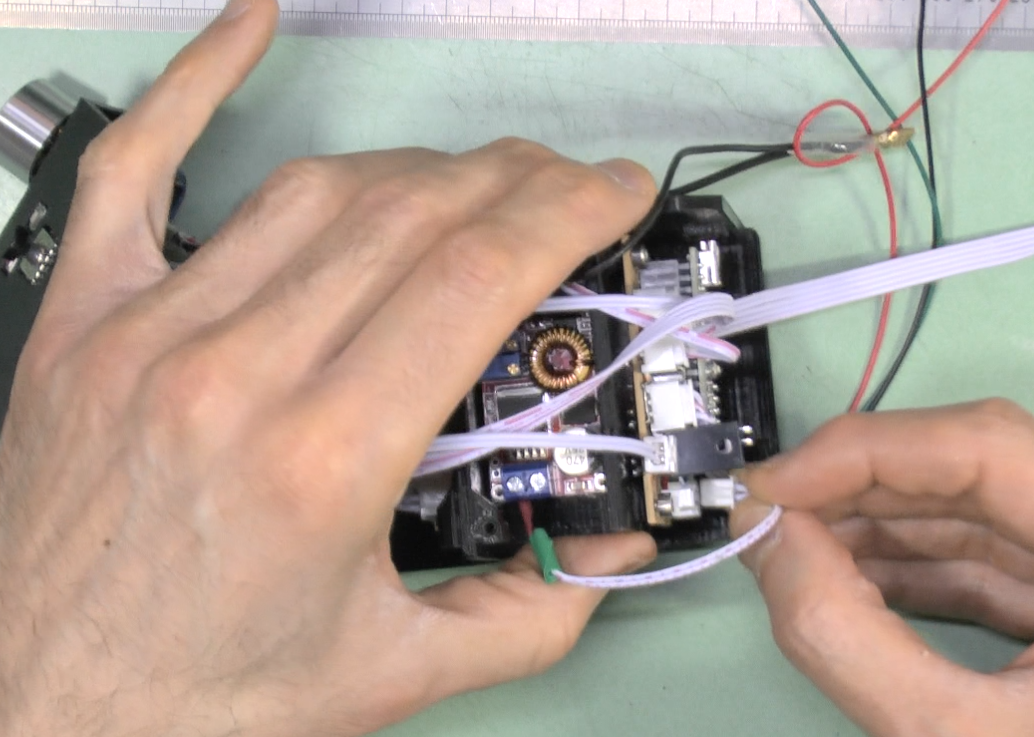
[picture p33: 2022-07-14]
Electronics/Control_Console/Images/JST3.png

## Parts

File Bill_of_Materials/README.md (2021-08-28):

Bill of Materials for the PUMA Microscope
=========================================

The spreadsheet herein gives detailed information on the types and numbers of 3D printed models and non-printed materials (nuts, bolts, optics, *etc.*) required to build various PUMA systems. Example sources where you can purchase non-printed items are also given. Where items are common, example purchase sources are simply stated as 'General Hardware store' or similar. Where items are more specialised then example seller URLs are given (mostly for AliExpress and eBay sellers).
**Please note that a link to a particular seller does NOT imply any guarantee of quality or reliability or best price or similar endorsement of that seller.**

The prefix MD_ is used to specify a PUMA module.

The prefix CF_ is used to specify a PUMA configuration.

A configuration is a whole working microscope which is made up of various modules.

Information is also provided about the weight of parts, modules and configurations. These weights are approximate.

This file does not include information about how to construct the modules.

Disclaimer
----------
This is a complex and detailed document and errors or omissions may have been made. If these are pointed out to me or otherwise come to light in future I will be happy to correct them but as with all the PUMA project, those who chose to build a PUMA system do so at their own risk.

PJT 28/08/2021

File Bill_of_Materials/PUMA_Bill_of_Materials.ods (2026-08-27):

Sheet: Non_Printed_Parts
Non-Printed Parts and Examplar Suppliers
NOTE: Exemplar supplier info DOES NOT imply reliability, superiority, quality or other endorsement of the given example supplier. Use at your own risk - esp. as product spec and quality may change over time.
NOTE: The links provided may be for purchase of multiple units – make sure you select the correct quantity you need if you buy from these links.
Non-Printed Fixings in A2 (ASTM-304) stainless steel. | Example supplier | Weight each g
Length of threaded shaft |  |  |  | 5 mm | 6 mm | 8 mm | 10 mm | 12 mm | 14 mm | 16 mm | 18 mm | 20 mm
M3_CSK_Allen_Bolt_12mm_long | General hardware store | 0.6
M4_CSK_Allen_Bolt_20mm_long | General hardware store | 1.9
M3_Hex_Head_Set_Screw_10mm_long | General hardware store | 0.8
M4_Hex_Head_Set_Screw_12mm_long | General hardware store | 1.8
M2_Allen_Bolt_Socket_Cap_DIN912_5mm_long | General hardware store | 0.21 | SLM, power board in PCC
M2_Allen_Bolt_Socket_Cap_DIN912_6mm_long | General hardware store | 0.24 | SLM, power board in PCC
M2_Allen_Bolt_Socket_Cap_DIN912_8mm_long | General hardware store | 0.27 | Piezo
M2_Allen_Bolt_Socket_Cap_DIN912_10mm_long | General hardware store | 0.31 | FB_Infinity_adapter.stl
M2_Allen_Bolt_Socket_Cap_DIN912_12mm_long | General hardware store | 0.35 | FB_Side_port_separate.stl, FB_Top_connector.stl, DI_Epi_pol.stl, DI_Pol_to_baseplate.stl
M3_Allen_Bolt_Socket_Cap_DIN912_5mm_long | General hardware store | 0.64 |  |  |  |  |  |  |  | 0.15 | 0.16 | 0.16
M3_Allen_Bolt_Socket_Cap_DIN912_6mm_long | General hardware store | 0.69
M3_Allen_Bolt_Socket_Cap_DIN912_8mm_long | General hardware store | 0.76
M3_Allen_Bolt_Socket_Cap_DIN912_10mm_long | General hardware store | 0.875
M3_Allen_Bolt_Socket_Cap_DIN912_12mm_long | General hardware store | 0.9333
M3_Allen_Bolt_Socket_Cap_DIN912_14mm_long | General hardware store | 1
M3_Allen_Bolt_Socket_Cap_DIN912_16mm_long | General hardware store | 1.1
M3_Allen_Bolt_Socket_Cap_DIN912_50mm_long | General hardware store | 2.9
M4_Allen_Bolt_Socket_Cap_DIN912_14mm_long | General hardware store | 1.9
M3_Grub_Screw_Cup_point_Hex_socket_DIN916_5mm_long | General hardware store | 0.15
M4_Grub_Screw_Cup_point_Hex_socket_DIN916_5mm_long | General hardware store | 0.276
M6_Grub_Screw_Cup_point_Hex_socket_DIN916_20mm_long | General hardware store | 3
M3_Pozi_Pan_Head_Machine_Screw_DIN7985_30mm_long | General hardware store | 1.67
M4_Pozi_Pan_Head_Machine_Screw_DIN7985_6mm_long | General hardware store | 1.2 | for mirror
M4_Pozi_Pan_Head_Machine_Screw_DIN7985_10mm_long | General hardware store | 1.6 | for z motor
M4_Pozi_Pan_Head_Machine_Screw_DIN7985_12mm_long | General hardware store | 1.8 | for xy stabiliser
M4_Pozi_Pan_Head_Machine_Screw_DIN7985_14mm_long | General hardware store | 1.9 | for AR stay thumbwheel stabiliser
M4_Pozi_Pan_Head_Machine_Screw_DIN7985_16mm_long | General hardware store | 2 | for eccentric tensioners and stabiliser
M4_Pozi_Pan_Head_Machine_Screw_DIN7985_20mm_long | General hardware store | 2.5
M4_Pozi_Pan_Head_Machine_Screw_DIN7985_25mm_long | General hardware store | 2.8
M6_Hex_Head_Bolt_Fully_Threaded_12mm_long | General hardware store | 4.25
M6_Hex_Head_Bolt_Fully_Threaded_16mm_long | General hardware store | 5.3
M6_Hex_Head_Bolt_Fully_Threaded_20mm_long | General hardware store | 5.6
M6_Hex_Head_Bolt_Fully_Threaded_30mm_long | General hardware store | 7.2
M6_Hex_Head_Bolt_Fully_Threaded_35mm_long | General hardware store | 8
M6_Hex_Head_Bolt_Fully_Threaded_45mm_long | General hardware store | 9.75
M6_Hex_Head_Bolt_Fully_Threaded_55mm_long | General hardware store | 12.3
M6_Hex_Head_Bolt_Fully_Threaded_70mm_long | General hardware store | 14.5
M6_Hex_Head_Bolt_Part_Threaded_DIN931_50mm_long | General hardware store | 12.4
M6_Allen_socket_Pan_screw_Fully_Threaded_10mm_long |  | 3
M6_Pozi_Pan_screw_Fully_Threaded_16mm_long | General hardware store | 5.6
M6_Pozi_Pan_screw_Fully_Threaded_20mm_long | General hardware store | 5.88
M6_Hex_threaded_standoff_25mm_long | General hardware store | 12
M6_Wing_nuts | General hardware store | 4.8
M6_Hex_socket_button_head_screw_10mm_long | https://www.ebay.co.uk/itm/222691855666?var=521546670983 | 3
M6_T_Nuts_for_2020_Extrusion | CNC Parts Store | 1
M2_Full_Nut | General hardware store | 0.11
M3_Full_Nut | General hardware store | 0.3
M4_Full_Nut | General hardware store | 0.75
M6_Full_Nut | General hardware store | 2.1
M6_nyloc_locking_nut | General hardware store | 2.3
M6_20mm_Hex_Steel_Spacer_20mm_long | RS Pro 603-536 https://uk.rs-online.com/web/p/enclosure-accessories/0603536 | 13.3333
M2_Washer_Flat_FormA_DIN125 | General hardware store | 0.03
M3_Washer_Flat_FormA_DIN125 | General hardware store | 0.075
M4_Washer_Flat_FormA_DIN125 | General hardware store | 0.26
M6_Washer_Flat_FormA_DIN125 | General hardware store | 0.9
M6_Washer_Penny_Repair_1.5_x_25 | eBay e.g. https://www.ebay.co.uk/itm/221061609656 | 4.6
M6_Washer_Penny_Repair_1.5_x_20 | Ebay e.g. https://www.ebay.co.uk/itm/221296544259?var=522379456556 | 2.1
No.12_M6_Cup_washer | eBay e.g. https://www.ebay.co.uk/itm/111304110685 | 0.95
M6_Plastic_Head_cap | eBay e.g. https://www.ebay.co.uk/itm/162725704664 | 0.5
corner_bracket_for_2020_extrusion | CNC Parts Store | 5.3
2020_Alu_extrusion_90mm | CNC Parts Store | 35
2020_Alu_extrusion_70mm | CNC Parts Store | 26
2020_Alu_extrusion_210mm | CNC Parts Store | 80
2020_Alu_extrusion_290mm | CNC Parts Store | 112
DIN_Rail_Steel_M6_holes_200mm_long | https://www.aliexpress.com/item/1005003134385396.html | 57
Steel_Tee_plates_75mm | https://cpc.farnell.com/duratool/d01072/75mm-tee-plates-b-z-y-pk10/dp/FN02117 | 30
Timing_belt_GT2_300mm_long_closed_loop_6mm_wide | AliExpress e.g. https://www.aliexpress.com/item/32950422029.html | 1
Spring_StainlessSteel_Compression_0.8guage_x10diam_x20long | AliExpress e.g. https://www.aliexpress.com/item/1005001408406253.html | 0.7
Stage_clips_pair_5.5cm | AliExpress e.g. https://www.aliexpress.com/item/32979312478.html | 11.3
Vernier_caliper | eBay e.g. https://www.ebay.co.uk/itm/323159213051 | 118
JST Cable (various pin numbers) | General Electronics stores | 3.5
JST Connector PCB mount (variousnumbers) | General Electronics stores | 0.5
PTFE_Ferrule_8mmOD_6mmID_8mmLong | AliExpress e.g. https://www.aliexpress.com/item/33064459360.html | 0.6 | for PCC trimpot control
PTFE_Ferrule_8mmOD_6mmID_5mmLong | https://www.aliexpress.com/item/1005009249548463.html | 0.5
PTFE_Ferrule_8mmOD_6mmID_2mmLong | AliExpress e.g. https://www.aliexpress.com/item/33064459360.html | 0.2
28BYJ48 Stepper Motor | AliExpress e.g. for 5V version https://www.aliexpress.com/item/4001007552575.html or for 12V version this: https://www.aliexpress.com/item/1005001388246118.html | 34
Power_regulator_constant_current_constant_voltage_buck_converter | AliExpress e.g. https://www.aliexpress.com/item/32764692383.html | 19.64
Joystick board | AliExpress e.g. https://www.aliexpress.com/item/32962961376.html | 4.8
Stepper controller board | AliExpress e.g. https://www.aliexpress.com/item/1005001698595944.html | 5
Bourns potentiometer | eBay e.g. https://www.ebay.co.uk/itm/184032345784 | 19
ON/OFF switch | Amazon e.g. https://www.amazon.co.uk/gp/product/B076GXD7XN/ | 3
Phono plug | General Electronics stores | 2.95
Phono socket | AliExpress e.g. https://www.aliexpress.com/item/4000672670954.html | 2.2
Piezo buzzer passive 30mm x 5.5 mm AT3040 | eBay e.g. https://www.ebay.co.uk/itm/193578806777 | 4.15
9v connector | General Electronics stores | 2.28
LED bulb | AliExpress e.g. https://www.aliexpress.com/item/32881415165.html?spm=a2g0s.9042311.0.0.27424c4dtwn5d8 or https://www.aliexpress.com/item/4001197438816.html?spm=a2g0s.9042311.0.0.27424c4dZectqS | 0.33
TFT display ST7789 | AliExpress e.g. https://www.aliexpress.com/item/4000182036178.html | 4.5
P-Channel MOSFET, 78 A, 60 V, 3-Pin TO-220F ON Semiconductor BMS3003-1E or equivalent | RS 862-8766 https://uk.rs-online.com/web/p/mosfets/8628766 | 1.75
Arduino Nano | General Electronics stores | 5.7
PCB DIL socket for Arduino nano | General Electronics stores | 2.5
Tripad board | General Electronics stores | 5
Twin-cable (figure-8) for LED power cord: each conductor made of 13 strands of copper (overall 0.7mm diameter), insulation 0.7 mm thick, overall cross sectional dimensions for both conductors with insulation = 2.2X4.4 mm | General Electronics stores | 5
Resistor 1 W through hole ohmage as per circuit diagram | General Electronics stores | 1
spade terminal connector sizes as per electronics construction guides | General Electronics stores | 0.5
Counterweight_for_XY_Table_of_CNC_Stage | General hardware store | 268
NEMA11_Stepper_with_Gearbox_1.518:1_Ratio | https://www.aliexpress.com/item/32961206942.html | 240
DM320T_Digital_Stepper_Driver_Unit | https://www.aliexpress.com/item/32839248983.html | 90
Rigid_shaft_coupler_14mmDia_6mm_to_7mm | https://www.ebay.co.uk/itm/284102430715?var=586471865504 | 8 | Comes with its own grub screws so those are not included in the worksheets
Optical_endstop_sensor_limit_switch | https://www.aliexpress.com/item/32852113543.html | 11
PTFE_Bowden_tube_ID2_OD4_43mm_long | https://www.aliexpress.com/item/1005008619424099.html | 0.8 | This is standard Bowden tube for 1.75 mm diameter filament.
Teflon_PTFE_Washer_OD12mm_ID7mm_thickness1mm | https://www.ebay.co.uk/itm/143414788394?var=442354991308 | 0.1
ManganeseSteel_WaveSpringCrinkle_Washer_M8 | https://www.ebay.co.uk/itm/165831249222?var=465334138887 | 0.1
Plywood_base_board_400mmx300mmx12mm | General hardware store | 1000
Arduino_Mega_2560 |  | 37
PSU_24V_15Amp_360W_Regulated |  | 500
DuPont_Connectors_Pack_male_to_male |  | 100
Aluminium_foil_self_adhesive |  | 0.1
USB_Cable_from_Arduino_to_PC |  | 25
Mains_cable_and_plug_for_PSU |  | 100
Wires_to_connect_PSU_to_Stepper_drivers |  | 50
Coaxial_cable_to_get_shielding_mesh_from |  | 100
XY_Table_for_CNC_150_x_210_mm | https://www.aliexpress.com/item/1005006117006289.html | 4000
Z_Mechanism_LZ60-2_for_CNC | https://www.aliexpress.com/item/1005005287095750.html | 390
Veroboard-type stripboard | Various lab suppliers including on eBay and AliExpress
Headers for Veroboard (for Aperta Control console) | https://www.aliexpress.com/item/4000873858801.html
ESP32-S3 N16R8 DevkitC-1 | https://www.aliexpress.com/item/1005006737960797.html
USB A to C (for ESP32 board) | https://www.aliexpress.com/item/1005006282457529.html
USB A sockets | https://www.aliexpress.com/item/4001104029052.html
9V Battery 6LR61 | General Electronics stores | 45
Eyepiece to fit a tube of diameter of 23.2 mm | Any source | 59
Objective x40, RMS thread, 160 mm or 170 mm mechanical tube length and 195 mm conjugate focal distance | Any source | 59
Oval Mirror (“Small 5.5x4x0.1 cm” if buying from the example link) | AliExpress e.g. https://www.aliexpress.com/item/4000522518566.html | 4.6
Microscope slide with coverslip | Various lab suppliers including on eBay and AliExpress | 5.75
Lens condenser 23 | 23 mm diameter lens from here https://www.ebay.co.uk/itm/261504712347 | 4.1
Lens condenser 30 (paraboloid) | 30 mm diameter lens from here | 13
Lens condenser 30 (spherical) | 30 mm diameter lens from here https://www.ebay.co.uk/itm/264087225310 | 13
Lens condenser 44 | 44 mm diameter lens from here https://www.aliexpress.com/item/32949791660.html?spm=a2g0s.9042311.0.0.27424c4dWXwBVh | 33
Lens D=23mm, f=60 mm (low power Kohler) | AliExpress e.g. https://www.aliexpress.com/item/1005001321078189.html | 1.6
Filter fluo yellow (510nm long pass 17 mm diameter 1.5 mm thick) | AliExpress e.g. https://www.aliexpress.com/item/4001058681187.html | 0.85
Filter fluo blue (450nm narrow band pass 14 mm diameter x 1 mm thick) | AliExpress e.g. https://www.aliexpress.com/item/32915657340.html | 0.85
Lens Infinity tube f=100 mm, 25 mm diameter, upto 6 mm thick | Any supplier including AliExpress stores | 9.5
Mirror_2cm_square_first_surface_full_2mm_thick | AliExpress e.g. https://www.aliexpress.com/item/4000448280628.html | 2
Mirror_25mm_round_first_surface_full_Molybdenum_3mm_thick | AliExpress e.g. https://www.aliexpress.com/item/32234558080.html | 15
Beamsplitter_glass_2cm_square_1.1mm_thick | AliExpress e.g. https://www.aliexpress.com/item/4000686997942.html | 1
Polarising film for polariser 0.7 mm thick (no adhesive, protective film on both sides) | AliExpress e.g. https://www.aliexpress.com/item/32809585908.html | 1 | Thickness is for strength to avoid floppy deformation – can be any similar thickness but not more than 0.9 mm or will not fit filter trays.
Polarising film for analyser 0.13 mm thick (no adhesive, protective film on both sides) | AliExpress e.g. https://www.aliexpress.com/item/32809585908.html | 0.5 | Thinness is to avoid the need to lower trhe condenser too much when used with DI_Uber_pol. Can by any similar thickness – the thinner the better.
Negative lens for AR projector: H-ZF2/H-K10 glass achromatic doublet, diameter = 26.3 mm, f= -55.6 mm | AliExpress e.g. https://www.aliexpress.com/item/4001131525716.html | 9.5
Positive lens for AR Projector: Achromatic doublet cemented glass, diameter 17 mm, f= 51.98 mm | AliExpress e.g. https://www.aliexpress.com/item/1005001346038314.html | 9.5
Fresnel lens, round, 2 mm thick, 100 mm diameter, 50 mm focal length | AliExpress e.g. https://www.aliexpress.com/item/32783160945.html | 15 | for PCC monitor

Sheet: MD_CNC_Stage
Resources for making the precision CNC stage (motorised on all axes)
Printed Parts
Model | Time_Hr | Time_Min | PLA_Length(m) |  | Quantity_required |  | Subtotal_Hr | Subtotal_Minutes | Subtotal_PLA_length
CN_Ardu_bus_bar_mount | 7 | 29 | 20.74 |  | 1 |  | 7 | 29 | 20.74
CN_Ardu_Bus_Clip_set | 4 | 13 | 6.1 |  | 1 |  | 4 | 13 | 6.1
CN_Ardu_M3_Washer | 0 | 1 | 0.02 |  | 1 |  | 0 | 1 | 0.02
CN_BB_Jig_Back_Left | 5 | 10 | 12.8 |  | 2 |  | 10 | 20 | 25.6
CN_BB_Jig_Back_Measure | 1 | 13 | 3.02 |  | 1 |  | 1 | 13 | 3.02
CN_BB_Jig_Back_Right | 5 | 10 | 12.8 |  | 1 |  | 5 | 10 | 12.8
CN_BB_Jig_Front_Left | 4 | 57 | 12.47 |  | 3 |  | 12 | 171 | 37.41
CN_BB_Jig_Front_Measure | 0 | 17 | 0.87 |  | 1 |  | 0 | 17 | 0.87
CN_BB_Jig_Front_Right | 4 | 57 | 12.47 |  | 1 |  | 4 | 57 | 12.47
CN_BB_Jig_Left_Measure | 1 | 22 | 3.6 |  | 1 |  | 1 | 22 | 3.6
CN_BB_Jig_Right_Measure | 1 | 22 | 3.6 |  | 1 |  | 1 | 22 | 3.6
CN_BB_Jig_Undercarriage | 4 | 49 | 12.12 |  | 1 |  | 4 | 49 | 12.12
CN_BB_Jig_XYTable | 5 | 33 | 13.98 |  | 2 |  | 10 | 66 | 27.96
CN_BB_Jig_Y_Lim | 0 | 38 | 2.09 |  | 1 |  | 0 | 38 | 2.09
CN_F_Ardu_strut_BL | 1 | 49 | 5.8 |  | 1 |  | 1 | 49 | 5.8
CN_F_Ardu_strut_BR | 1 | 49 | 5.8 |  | 2 |  | 2 | 98 | 11.6
CN_F_Ardu_strut_TL | 1 | 49 | 5.8 |  | 2 |  | 2 | 98 | 11.6
CN_F_Ardu_strut_TR | 1 | 49 | 5.8 |  | 1 |  | 1 | 49 | 5.8
CN_F_DM3_Mount | 2 | 12 | 6.32 |  | 1 |  | 2 | 12 | 6.32
CN_F_DPST_to_2020 | 2 | 22 | 5.89 |  | 1 |  | 2 | 22 | 5.89
CN_F_OM_QR_Plate | 9 | 43 | 27.37 |  | 1 |  | 9 | 43 | 27.37
CN_F_Overmount | 9 | 33 | 26.48 |  | 1 |  | 9 | 33 | 26.48
CN_F_RAMPS_clamp_Left | 1 | 35 | 4.2 |  | 1 |  | 1 | 35 | 4.2
CN_F_RAMPS_clamp_Right | 1 | 35 | 4.2 |  | 1 |  | 1 | 35 | 4.2
CN_F_UM_Opt_gripper | 1 | 42 | 4.61 |  | 1 |  | 1 | 42 | 4.61
CN_F_UM_Opt_Gripper_washer | 0 | 3 | 0.16 |  | 1 |  | 0 | 3 | 0.16
CN_F_UM_Opt_to_QR_F | 2 | 40 | 7.81 |  | 1 |  | 2 | 40 | 7.81
CN_F_Undercarriage_platform | 8 | 36 | 23.99 |  | 4 |  | 32 | 144 | 95.96
CN_PSU_CableFixture_front | 9 | 1 | 29.11 |  | 1 |  | 9 | 1 | 29.11
CN_PSU_DC_CableCover | 0 | 32 | 1.66 |  | 1 |  | 0 | 32 | 1.66
CN_PSU_Mains_CableCover | 1 | 1 | 2.99 |  | 1 |  | 1 | 1 | 2.99
CN_PSU_Peg_Leg | 0 | 9 | 0.3 |  | 1 |  | 0 | 9 | 0.3
CN_Sam_Counter_weight | 1 | 6 | 3.15 |  | 1 |  | 1 | 6 | 3.15
CN_Sam_Pincer_Extn1_L | 0 | 52 | 2.3 |  | 1 |  | 0 | 52 | 2.3
CN_Sam_Pincer_Extn1_R | 0 | 52 | 2.3 |  | 1 |  | 0 | 52 | 2.3
CN_Sam_Pincer_Extn2_L | 1 | 24 | 3.92 |  | 1 |  | 1 | 24 | 3.92
CN_Sam_Pincer_Extn2_R | 1 | 24 | 3.94 |  | 1 |  | 1 | 24 | 3.94
CN_Sam_Presser_wings | 0 | 53 | 2.47 |  | 1 |  | 0 | 53 | 2.47
CN_Sam_Spring_arm_assy | 6 | 1 | 15.43 |  | 1 |  | 6 | 1 | 15.43
CN_Sam_Stage_Top | 11 | 0 | 28.98 |  | 1 |  | 11 | 0 | 28.98
CN_SD_2020_End_cap | 0 | 13 | 0.46 |  | 1 |  | 0 | 13 | 0.46
CN_SD_2020_Protector | 0 | 23 | 0.9 |  | 1 |  | 0 | 23 | 0.9
CN_SD_Aft_clip | 0 | 5 | 0.07 |  | 1 |  | 0 | 5 | 0.07
CN_SD_Aft_Hole_cover | 0 | 34 | 1.84 |  | 1 |  | 0 | 34 | 1.84
CN_SD_Aft_Left | 16 | 13 | 67.98 |  | 1 |  | 16 | 13 | 67.98
CN_SD_Aft_Mid | 14 | 55 | 54.11 |  | 1 |  | 14 | 55 | 54.11
CN_SD_Aft_Right | 16 | 12 | 67.98 |  | 1 |  | 16 | 12 | 67.98

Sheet: MD_Stage
Resources for making the stage (no motor unit)
Printed Parts
Model | Time_Hr | Time_Min | PLA_Length(m) |  | Quantity_required |  | Subtotal_Hr | Subtotal_Minutes | Subtotal_PLA_length
ST_BasePlate | 8 | 33 | 25.63 |  | 1 |  | 8 | 33 | 25.63
ST_FocusPlate | 4 | 8 | 11.22 |  | 1 |  | 4 | 8 | 11.22
ST_Articulation | 0 | 14 | 0.53 |  | 3 |  | 0 | 42 | 1.59
FG_Fine_gear | 1 | 38 | 2.65 |  | 1 |  | 1 | 38 | 2.65
FG_Focus_spacer | 0 | 20 | 0.7 |  | 2 |  | 0 | 40 | 1.4
FG_Intermedius | 1 | 7 | 1.75 |  | 1 |  | 1 | 7 | 1.75
FG_Pulley_coarse | 1 | 18 | 2.03 |  | 1 |  | 1 | 18 | 2.03
FG_Pulley | 0 | 21 | 0.33 |  | 2 |  | 0 | 42 | 0.66
FG_Eccentric_Tensioner_Top | 0 | 24 | 0.69 |  | 3 |  | 0 | 72 | 2.07
FG_Eccentric_Tensioner_Bottom | 0 | 19 | 0.44 |  | 3 |  | 0 | 57 | 1.32
FG_Eccentric_Tensioner_Pulley_c_adhesin | 0 | 17 | 0.22 |  | 3 |  | 0 | 51 | 0.66
 |  |  |  |  |  |  |  |  | Total Weight of filament (g)
 |  |  |  |  |  |  |  |  | 152.05037480999
Non-Printed Parts (NPP) |  | Weight_each_g |  |  |  |  |  |  | Subtotal_weight
PTFE_Ferrule_8mmOD_6mmID_5mmLong |  | 0.5 |  |  | 3 |  |  |  | 1.5
Spring_StainlessSteel_Compression_0.8guage_x10diam_x20long |  | 0.7 |  |  | 3 |  |  |  | 2.1
M6_nyloc_locking_nut |  | 2.3 |  |  | 3 |  |  |  | 6.9
Timing_belt_GT2_300mm_long_closed_loop_6mm_wide |  | 1 |  |  | 1 |  |  |  | 1
M6_Full_Nut |  | 2.1 |  |  | 9 |  |  |  | 18.9
M6_Washer_Flat_FormA_DIN125 |  | 0.9 |  |  | 10 |  |  |  | 9
M6_Washer_Penny_Repair_1.5_x_25 |  | 4.6 |  |  | 2 |  |  |  | 9.2
M6_Hex_Head_Bolt_Fully_Threaded_16mm_long |  | 5.3 |  |  | 2 |  |  |  | 10.6
M6_Hex_Head_Bolt_Fully_Threaded_70mm_long |  | 14.5 |  |  | 3 |  |  |  | 43.5
M4_Full_Nut |  | 0.75 |  |  | 8 |  |  |  | 6
M4_Washer_Flat_FormA_DIN125 |  | 0.26 |  |  | 4 |  |  |  | 1.04
M4_Pozi_Pan_Head_Machine_Screw_DIN7985_16mm_long |  | 2 |  |  | 3 |  |  |  | 6
M3_Grub_Screw_Cup_point_Hex_socket_DIN916_5mm_long |  | 0.15 |  |  | 3 |  |  |  | 0.45
M6_Hex_Head_Bolt_Part_Threaded_DIN931_50mm_long |  | 12.4 |  |  | 2 |  |  |  | 24.8
No.12_M6_Cup_washer |  | 0.95 |  |  | 3 |  |  |  | 2.85
 | Module |  |  | Total_filament_length m |  | Total_weight_filament | Hrs | Mins | Total_Weight
Total_time_and_weight | Stage |  |  | 50.98 |  | 152.05037480999 | 21 | 48 | 295.89037480999

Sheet: MD_Stabiliser
Resources for making the stabiliser exoskeleton
Printed Parts
Model | Time_Hr | Time_Min | PLA_Length(m) |  | Quantity_required |  | Subtotal_Hr | Subtotal_Minutes | Subtotal_PLA_length
SB_S1_Axial.stl | 7 | 29 | 20.71 |  | 1 |  | 7 | 29 | 20.71
SB_S1_Insert_c_adhesin.stl | 0 | 32 | 0.96 |  | 1 |  | 0 | 32 | 0.96
SB_S1_Lateral_strut_Left.stl | 2 | 5 | 6.26 |  | 1 |  | 2 | 5 | 6.26
SB_S1_Lateral_strut_Right.stl | 2 | 6 | 6.26 |  | 1 |  | 2 | 6 | 6.26
SB_S1_Peg.stl | 0 | 16 | 0.44 |  | 1 |  | 0 | 16 | 0.44
 |  |  |  |  |  |  |  |  | Total Weight of filament (g)
 |  |  |  |  |  |  |  |  | 103.285690068065
Non-Printed Parts (NPP) |  | Weight_each_g |  |  |  |  |  |  | Subtotal_weight
M4_Full_Nut |  | 0.75 |  |  | 4 |  |  |  | 3
M4_Pozi_Pan_Head_Machine_Screw_DIN7985_16mm_long |  | 2 |  |  | 4 |  |  |  | 8
M3_Allen_Bolt_Socket_Cap_DIN912_12mm_long |  | 0.9333 |  |  | 1 |  |  |  | 0.9333
Optional parts are 4xM3 grub screws and 1xM4 grub screw, each about 5 mm long.
 | Module |  |  | Total_filament_length m |  | Total_weight_filament | Hrs | Mins | Total_Weight
Total_time_and_weight | Stabiliser |  |  | 34.63 |  | 103.285690068065 | 12 | 28 | 115.218990068065

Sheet: MD_XY_Calipers
Resources for making the XY moveable calipers slide manipulator
Printed Parts
Model | Time_Hr | Time_Min | PLA_Length(m) |  | Quantity_required |  | Subtotal_Hr | Subtotal_Min | Subtotal_PLA_length
XY_Stabiliser | 1 | 26 | 2.59 |  | 1 |  | 1 | 26 | 2.59
 |  |  |  |  |  |  |  |  | Total Weight of filament (g)
 |  |  |  |  |  |  |  |  | 7.724803271045
Non-Printed Parts (NPP) |  | Weight_each_g |  |  |  |  |  |  | Subtotal_weight
PTFE_Ferrule_8mmOD_6mmID_5mmLong |  | 0.5 |  |  | 1 |  |  |  | 0.5
M6_Hex_Head_Bolt_Fully_Threaded_16mm_long |  | 5.3 |  |  | 1 |  |  |  | 5.3
M4_Full_Nut |  | 0.75 |  |  | 2 |  |  |  | 1.5
M4_Pozi_Pan_Head_Machine_Screw_DIN7985_12mm_long |  | 1.8 |  |  | 3 |  |  |  | 5.4
 | Module |  |  | Total_filament_length m |  | Total_weight_filament | Hrs | Mins | Total_Weight
Total_time_and_weight | XY_Calipers |  |  | 2.59 |  | 7.724803271045 | 1 | 26 | 20.424803271045

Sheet: MD_Ocular
Resources for ocular lens WF x10, 20mm field of view, high eyepoint, 23.2 mm barrel, for 160 mm mechanical tube length or infinity
Printed Parts
Model | Time_Hr | Time_Min | PLA_Length(m) |  | Quantity_required |  | Subtotal_Hr | Subtotal_Min | Subtotal_PLA_length
MN_Ocular_cap | 0 | 42 | 1.65 |  | 1 |  | 0 | 42 | 1.65
MN_Ocular_lock_nut | 0 | 16 | 0.47 |  | 1 |  | 0 | 16 | 0.47
MN_Ocular_tube_protective_cap | 0 | 26 | 1.14 |  | 1 |  | 0 | 26 | 1.14
 |  |  |  |  |  |  |  |  | Total Weight of filament (g)
 |  |  |  |  |  |  |  |  | 9.72311145313
Non-Printed Parts (NPP) |  | Weight_each_g |  |  |  |  |  |  | Subtotal_weight
Eyepiece to fit a tube of diameter of 23.2 mm |  | 59 |  |  | 1 |  |  |  | 59
 | Module |  |  | Total_filament_length m |  | Total_weight_filament | Hrs | Mins | Total_Weight
Total_time_and_weight | Ocular_lens |  |  | 3.26 |  | 9.72311145313 | 1 | 24 | 68.72311145313

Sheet: MD_Legs_short
Resources for making the short legs with stage inclined to 35 degree
Printed Parts
Model | Time_Hr | Time_Min | PLA_Length(m) |  | Quantity_required |  | Subtotal_Hr | Subtotal_Min | Subtotal_PLA_length
LG_Short_leg | 0 | 16 | 0.54 |  | 3 |  | 0 | 48 | 1.62
 |  |  |  |  |  |  |  |  | Total Weight of filament (g)
 |  |  |  |  |  |  |  |  | 4.83173023131
Non-Printed Parts (NPP) |  | Weight_each_g |  |  |  |  |  |  | Subtotal_weight
M6_20mm_Hex_Steel_Spacer_20mm_long |  | 13.3333 |  |  | 3 |  |  |  | 39.9999
M6_Washer_Flat_FormA_DIN125 |  | 0.9 |  |  | 3 |  |  |  | 2.7
 | Module |  |  | Total_filament_length m |  | Total_weight_filament | Hrs | Mins | Total_Weight
Total_time_and_weight | Legs_short |  |  | 1.62 |  | 4.83173023131 | 0 | 48 | 47.53163023131

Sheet: MD_Legs_long_35
Resources for making the long legs inclining the stage 35 degrees
Printed Parts
Model | Time_Hr | Time_Min | PLA_Length(m) |  | Quantity_required |  | Subtotal_Hr | Subtotal_Min | Subtotal_PLA_length
LG_Front_legs | 3 | 21 | 9.34 |  | 1 |  | 3 | 21 | 9.34
LG_Back_leg_angled | 0 | 36 | 1.68 |  | 1 |  | 0 | 36 | 1.68
LG_Feet_linker | 3 | 18 | 8.43 |  | 1 |  | 3 | 18 | 8.43
 |  |  |  |  |  |  |  |  | Total Weight of filament (g)
 |  |  |  |  |  |  |  |  | 58.010588270975
Non-Printed Parts (NPP) |  | Weight_each_g |  |  |  |  |  |  | Subtotal_weight
M6_20mm_Hex_Steel_Spacer_20mm_long |  | 13.3333 |  |  | 3 |  |  |  | 39.9999
M6_Full_Nut |  | 2.1 |  |  | 6 |  |  |  | 12.6
M3_Hex_Head_Set_Screw_10mm_long |  | 0.6 |  |  | 1 |  |  |  | 0.6
M3_Allen_Bolt_Socket_Cap_DIN912_10mm_long | General hardware store | 0.875 |  |  | 4 |  |  |  | 3.5
M3_Full_Nut |  | 0.3 |  |  | 5 |  |  |  | 1.5
M3_Washer_Flat_FormA_DIN125 |  | 0.075 |  |  | 4 |  |  |  | 0.3
 | Module |  |  | Total_filament_length m |  | Total_weight_filament | Hrs | Mins | Total_Weight
Total_time_and_weight | Legs_long_35 |  |  | 19.45 |  | 58.010588270975 | 7 | 15 | 116.510488270975

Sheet: MD_Legs_long_level
Resources for making the long legs keeping the stage level
Printed Parts
Model | Time_Hr | Time_Min | PLA_Length(m) |  | Quantity_required |  | Subtotal_Hr | Subtotal_Min | Subtotal_PLA_length
LG_Front_legs | 3 | 21 | 9.34 |  | 1 |  | 3 | 21 | 9.34
LG_Back_leg_angled | 0 | 36 | 1.68 |  | 1 |  | 0 | 36 | 1.68
LG_Feet_linker | 3 | 18 | 8.43 |  | 1 |  | 3 | 18 | 8.43
LG_Hind_extension | 0 | 46 | 1.64 |  | 1 |  | 0 | 46 | 1.64
DI_M3_Thumbscrew_short_hex | 0 | 8 | 0.14 |  | 1 |  | 0 | 8 | 0.14
 |  |  |  |  |  |  |  |  | Total Weight of filament (g)
 |  |  |  |  |  |  |  |  | 63.319526426365
Non-Printed Parts (NPP) |  | Weight_each_g |  |  |  |  |  |  | Subtotal_weight
M6_20mm_Hex_Steel_Spacer_20mm_long |  | 13.3333 |  |  | 3 |  |  |  | 39.9999
M6_Full_Nut |  | 2.1 |  |  | 6 |  |  |  | 12.6
M6_Hex_Head_Bolt_Fully_Threaded_16mm_long |  | 5.3 |  |  | 1 |  |  |  | 5.3
M6_Plastic_Head_cap |  | 0.5 |  |  | 1 |  |  |  | 0.5
M3_Hex_Head_Set_Screw_10mm_long |  | 0.8 |  |  | 1 |  |  |  | 0.8
M3_Allen_Bolt_Socket_Cap_DIN912_10mm_long | General hardware store | 0.875 |  |  | 4 |  |  |  | 3.5
M3_Full_Nut |  | 0.3 |  |  | 5 |  |  |  | 1.5
M3_Washer_Flat_FormA_DIN125 |  | 0.075 |  |  | 4 |  |  |  | 0.3
M4_Grub_Screw_Cup_point_Hex_socket_DIN916_5mm_long | General hardware store | 0.276 |  |  | 1 |  |  |  | 0.276
 | Module |  |  | Total_filament_length m |  | Total_weight_filament | Hrs | Mins | Total_Weight
Total_time_and_weight | Legs_long_level |  |  | 21.23 |  | 63.319526426365 | 8 | 9 | 128.095426426365

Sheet: MD_Z_Motor
Resources for making the stage motorisation module
Printed Parts
Model | Time_Hr | Time_Min | PLA_Length(m) |  | Quantity_required |  | Subtotal_Hr | Subtotal_Min | Subtotal_PLA
ZM_Motor_attachment | 1 | 1 | 2.36 |  | 1 |  | 1 | 1 | 2.36
ZM_Motor_gear | 1 | 34 | 2.36 |  | 1 |  | 1 | 34 | 2.36
ZM_Z_Limit_Sw_Mount | 0 | 17 | 0.44 |  | 1 |  | 0 | 17 | 0.44
ZM_Z_Probe | 1 | 4 | 2.04 |  | 1 |  | 1 | 4 | 2.04
ZM_Z_Yoke | 0 | 22 | 0.66 |  | 1 |  | 0 | 22 | 0.66
 |  |  |  |  |  |  |  |  | Total Weight of filament (g)
 |  |  |  |  |  |  |  |  | 23.44283927043
Non-Printed Parts (NPP) |  | Weight_each_g |  |  |  |  |  |  | Subtotal_weight
PTFE_Ferrule_8mmOD_6mmID_5mmLong |  | 0.5 |  |  | 1 | For motor shaft |  |  | 0.5
PTFE_Ferrule_8mmOD_6mmID_2mmLong |  | 0.2 |  |  | 1 | For fine focus gear shaft |  |  | 0.2
M6_Hex_Head_Bolt_Fully_Threaded_16mm_long |  | 5.3 |  |  | 1 |  |  |  | 5.3
M4_Grub_Screw_Cup_point_Hex_socket_DIN916_5mm_long |  | 0.276 |  |  | 2 |  |  |  | 0.552
28BYJ48 Stepper Motor |  | 34 |  |  | 1 |  |  |  | 34
M3_Allen_Bolt_Socket_Cap_DIN912_6mm_long |  | 0.69 |  |  | 2 | To fix Z-probe to focus plate |  |  | 1.38
M3_Allen_Bolt_Socket_Cap_DIN912_10mm_long |  | 0.875 |  |  | 3 | Limit Sw hole closest to focus post, motor attachment to stage and Z-probe probe screw |  |  | 2.625
M3_Allen_Bolt_Socket_Cap_DIN912_14mm_long |  | 1 |  |  | 1 | Limit sw hole closest to intermediate gear |  |  | 1
M4_Pozi_Pan_Head_Machine_Screw_DIN7985_10mm_long |  | 1.6 |  |  | 2 | To fix motor to attachment |  |  | 3.2
JST Cable (various pin numbers) |  | 3.5 |  |  | 2 |  |  |  | 7
JST Connector PCB mount (variousnumbers) |  | 0.5 |  |  | 2 |  |  |  | 1
M4_Washer_Flat_FormA_DIN125 |  | 0.26 |  |  | 2 | To fix motor to attachment |  |  | 0.52
M4_Full_Nut |  | 0.75 |  |  | 2 |  |  |  | 1.5
 |  |  |  |  |  |  |  |  | 0
 | Module |  |  | Total_filament_length m |  | Total_weight_filament | Hrs | Mins | Total_Weight
Total_time_and_weight | Z_Motor |  |  | 7.86 |  | 23.44283927043 | 4 | 18 | 82.21983927043

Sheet: MD_DI_Mirror_simple
Resources for making the simple mirror illuminator (i.e. without condenser)
Printed Parts
Model | Time_Hr | Time_Min | PLA_Length(m) |  | Quantity_required |  | Subtotal_Hr | Subtotal_Min | Subtotal_PLA
DI_Cnd_Adj_thumbwheel | 0 | 8 | 0.26 |  | 4 |  | 0 | 32 | 1.04
DI_Mirror_holder_plain | 1 | 0 | 2.45 |  | 1 |  | 1 | 0 | 2.45
DI_Mirror_suspend_plain | 1 | 34 | 3.18 |  | 1 |  | 1 | 34 | 3.18
DI_Mirror_to_baseplate | 0 | 49 | 1.88 |  | 1 |  | 0 | 49 | 1.88
 |  |  |  |  |  |  |  |  | Total Weight of filament (g)
 |  |  |  |  |  |  |  |  | 25.500798443025
Non-Printed Parts (NPP) |  | Weight_each_g |  |  |  |  |  |  | Subtotal_weight
M4_Pozi_Pan_Head_Machine_Screw_DIN7985_6mm_long |  | 1.2 |  |  | 2 |  |  |  | 2.4
M4_Hex_Head_Set_Screw_12mm_long |  | 1.8 |  |  | 2 |  |  |  | 3.6
M4_Washer_Flat_FormA_DIN125 |  | 0.26 |  |  | 2 |  |  |  | 0.52
Oval Mirror (“Small 5.5x4x0.1 cm” if buying from the example link) |  | 4.6 |  |  | 1 |  |  |  | 4.6
 | Module |  |  | Total_filament_length m |  | Total_weight_filament | Hrs | Mins | Total_Weight
Total_time_and_weight | Mirror_Simple |  |  | 8.55 |  | 25.500798443025 | 3 | 55 | 36.620798443025
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

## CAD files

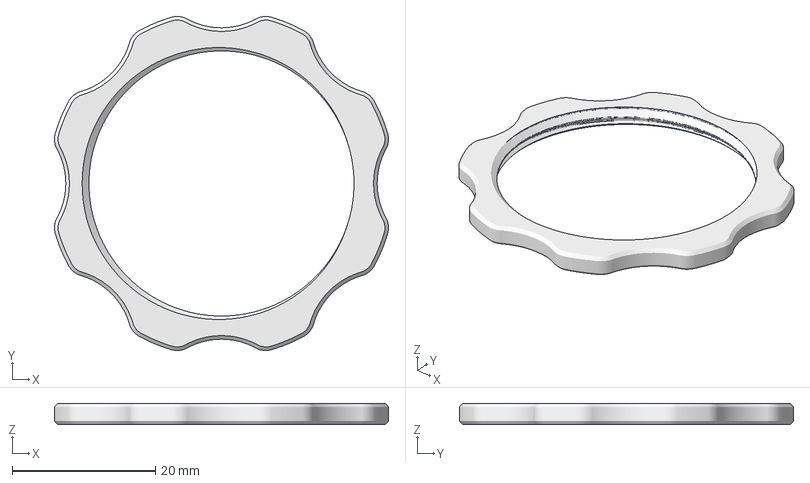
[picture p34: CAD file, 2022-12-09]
FreeCAD/CelestronXCelLX/Ocular_Locknut_XCelLX.FCStd
46.7 x 46.7 x 3.00 mm

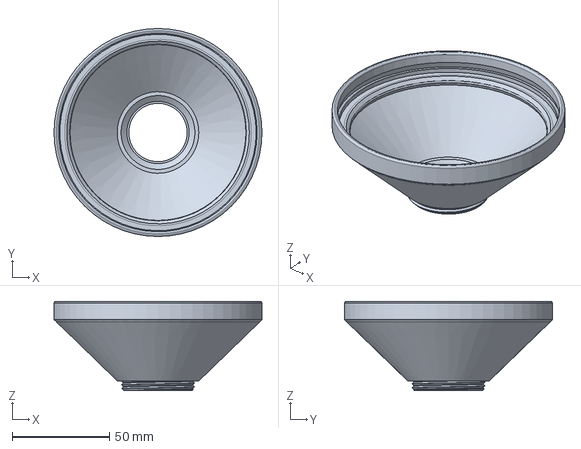
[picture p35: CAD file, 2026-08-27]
FreeCAD/PUMA_Aperta.FCStd
107.0 x 107.0 x 46.0 mm

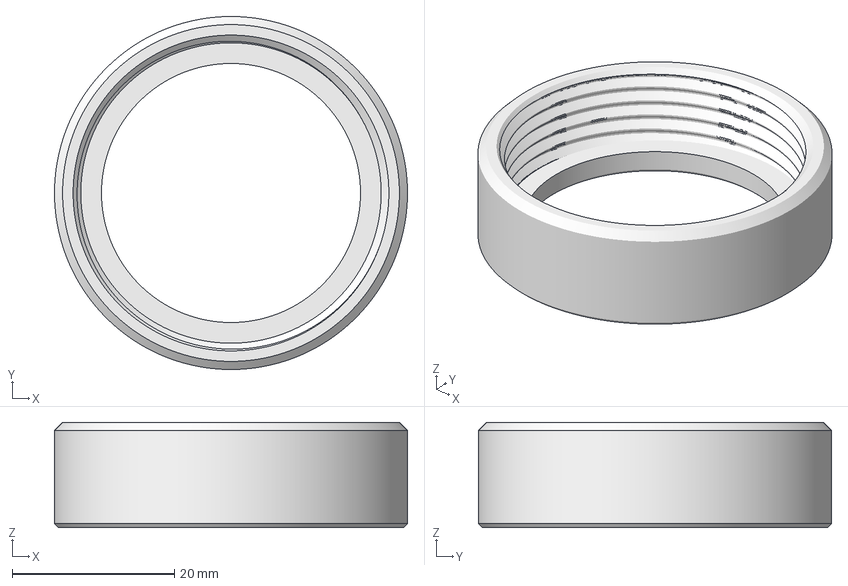
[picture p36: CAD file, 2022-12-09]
FreeCAD/CelestronXCelLX/Ocular_Cap_XCelLX.FCStd
43.6 x 43.6 x 13.0 mm

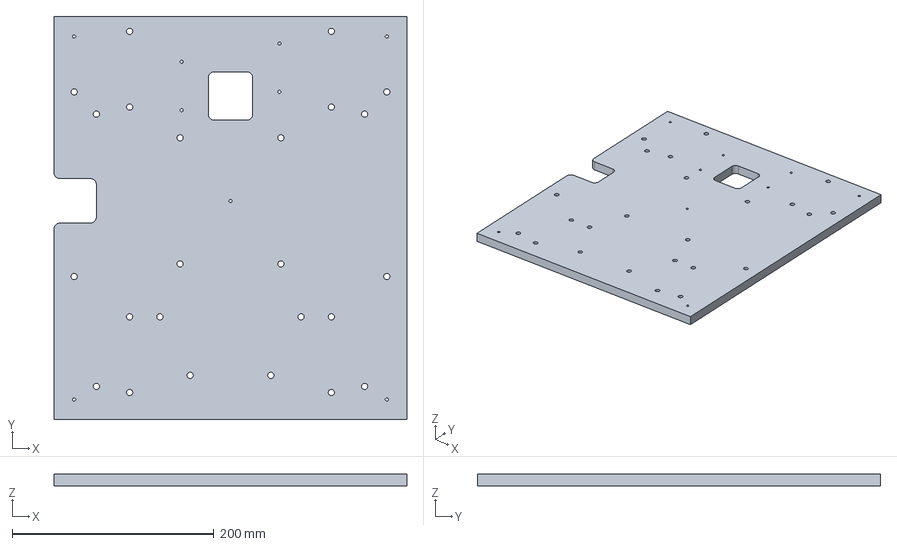
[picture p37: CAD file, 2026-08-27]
FreeCAD/CNC_Stage_Base_holes.FCStd
350.0 x 400.0 x 12.0 mm

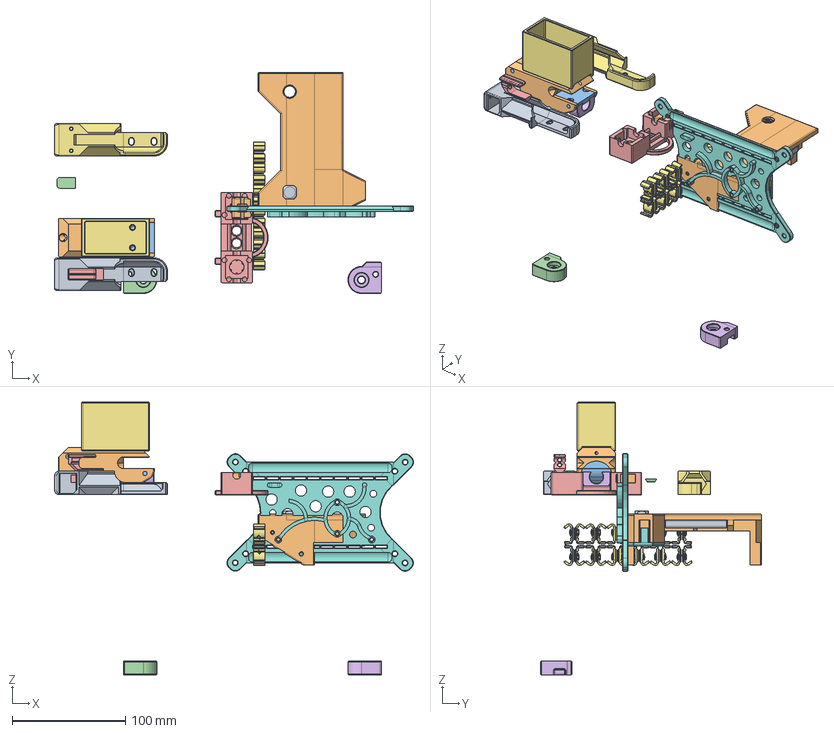
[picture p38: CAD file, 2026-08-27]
FreeCAD/CNC_Stage_1.FCStd
317.5 x 195.5 x 241.0 mm
X_Lim_sarcoph_R
X_ATLAS_M6_Axle_holder
XY_ATLAS_Spring_well_washer_1p5mm
XY_ATLAS_Spring_well_washer_3p0mm
XY_ATLAS_Spring_well_washer_2p0mm
XY_ATLAS_Spring_well_washer_2p5mm
X_NEMA11_CW_Hopper
Ardu_bus_bar_mount
PSU_DC_CableCover
PSU_CableFixture_front
Ardu_M3_Washer
X_Probe_Housing_R
X_Probe
XY_NEMA11_Undertable_Support
Ardu_Bus_Clip_set
PSU_Mains_CableCover
PSU_Peg_Leg
X_NEMA11_Bracket
X_NEMA11_Counter_weight
X_Probe_shim
X_ATLAS_base
X_Probe_Housing_L
X_Lim_sarcoph_L

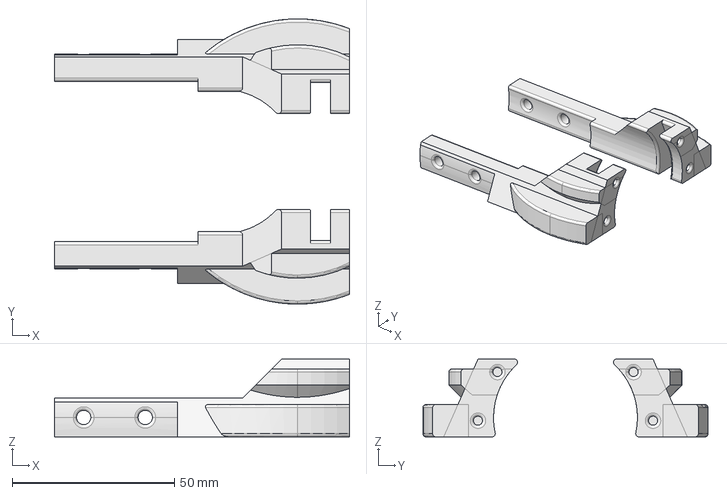
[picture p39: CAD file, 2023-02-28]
FreeCAD/Stabiliser.FCStd
91.0 x 88.0 x 24.0 mm

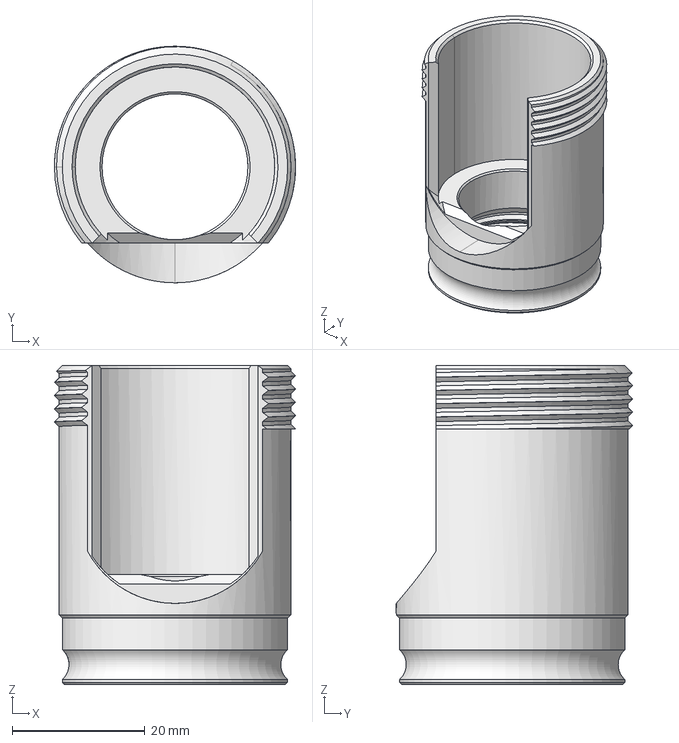
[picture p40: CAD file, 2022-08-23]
FreeCAD/Trinocular_CP.FCStd
36.4 x 35.7 x 48.1 mm

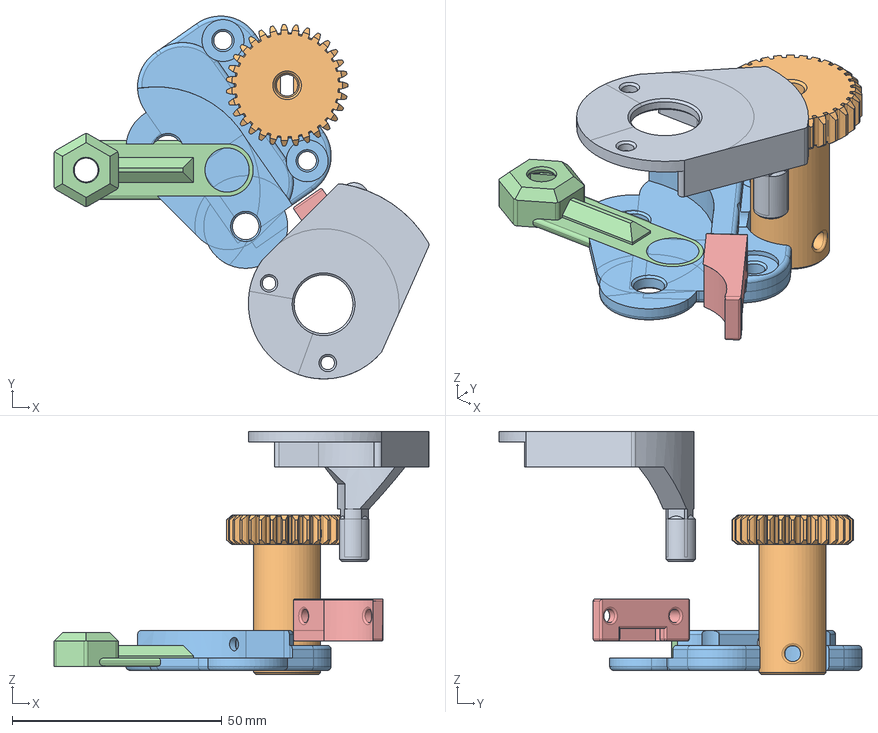
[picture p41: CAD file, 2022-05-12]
FreeCAD/Z_Motor.FCStd
89.4 x 86.5 x 58.0 mm
Z_Probe
Motor_gear
Motor_attachment
Z_Yoke
Z_Limit_Sw_mount

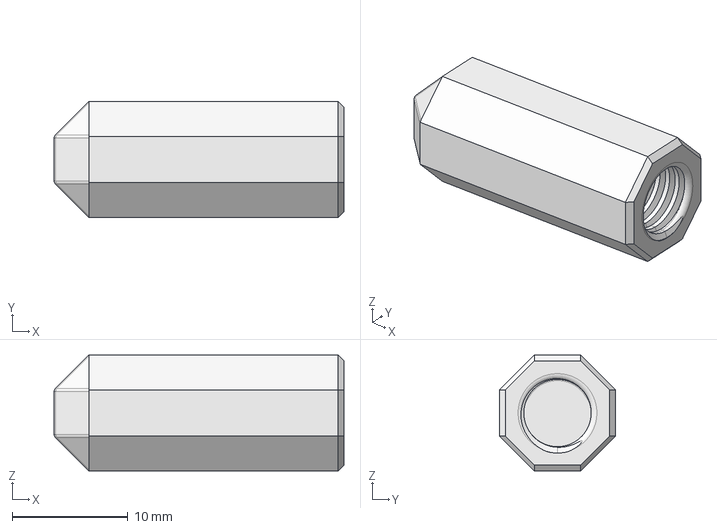
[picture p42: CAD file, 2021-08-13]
FreeCAD/Legs.FCStd
25.0 x 10.0 x 10.0 mm

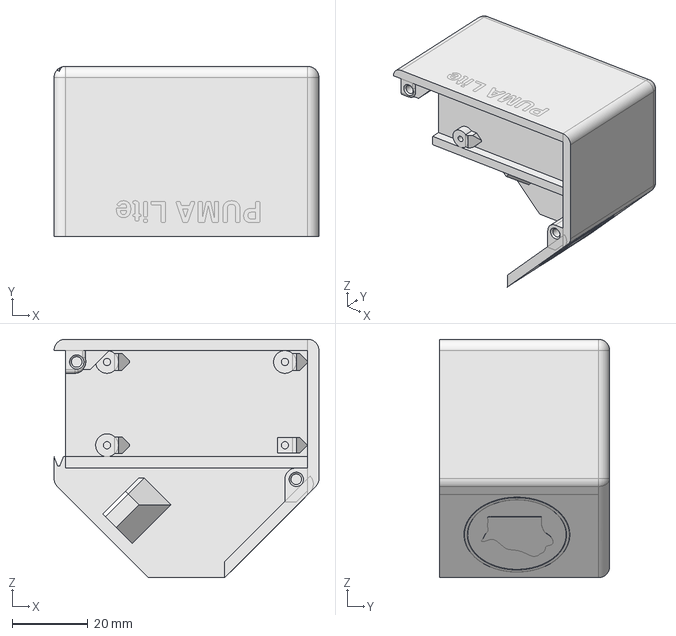
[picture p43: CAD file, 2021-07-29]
FreeCAD/PUMALite.FCStd
70.0 x 45.0 x 63.0 mm

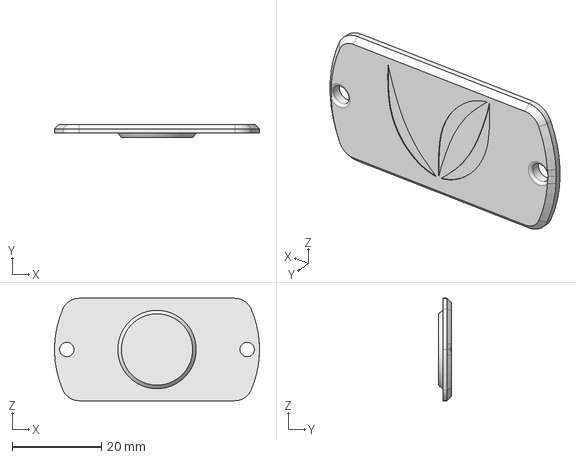
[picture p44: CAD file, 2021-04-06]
FreeCAD/Binocular_v3.1.FCStd
46.0 x 3.00 x 23.0 mm

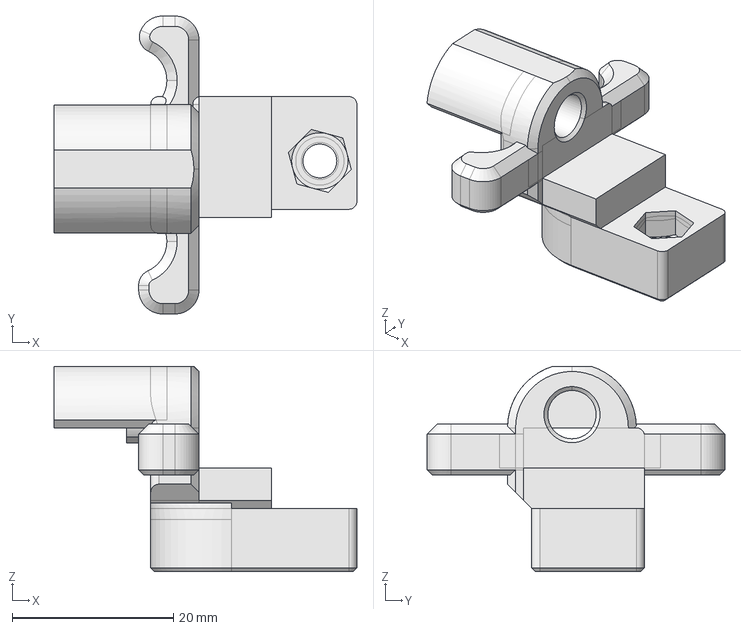
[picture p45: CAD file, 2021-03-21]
FreeCAD/XY_Stabiliser.FCStd
37.6 x 37.0 x 25.5 mm

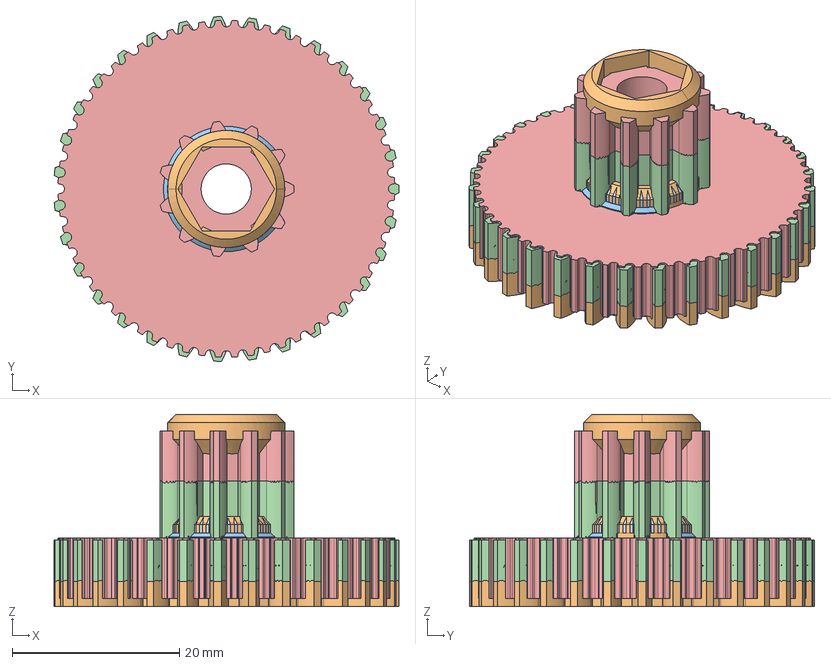
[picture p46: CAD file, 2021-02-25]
FreeCAD/Focus_Gears.FCStd
41.2 x 41.2 x 23.0 mm
Pulley
Pulley_coarse
Focus_spacer
Intermedius
Fine_knob

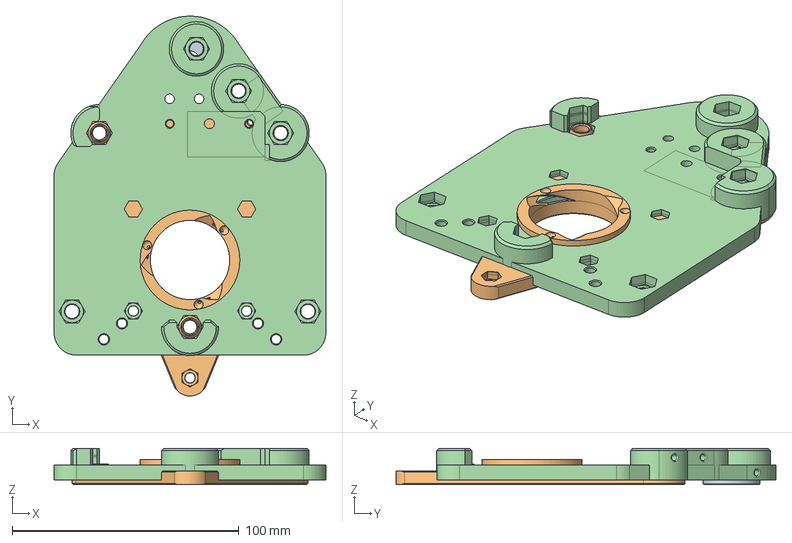
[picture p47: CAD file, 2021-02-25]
FreeCAD/Stage.FCStd
120.0 x 167.6 x 16.0 mm
Drilling_stabiliser
Focus_plate
Drilling_stabiliser_front
Base_plate

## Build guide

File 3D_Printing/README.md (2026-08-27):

PUMA 3D Printing Files
======================

This folder contains information about printing the 3D model files associated with the PUMA microscope project. 

STL files are not stored in the GitHub repository because many of them are too large (over 25 MB). However the information in the 'PUMA_3D_Printing_Guide' file explains how to generate the STL files (or other printable format files like .3mf) from the source (i.e. the CAD files) as well as giving information about how to print them. The information provided here relates to prints made with the Creality Ender 3 printer. Other printers may require modifications of the advice given.

The folder 'CE3_Cura' provides Cura (version 4.8.0) profiles that are suitable for the Creality Ender3 printer using standard PLA filament. If you don't use that printer or filament type then you would need to discover your own 'best' profiles for printing the models.

PJT 25.02.2021, last edit 27.08.2026.

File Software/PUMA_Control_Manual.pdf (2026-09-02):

# PUMA Control

## User’s Manual

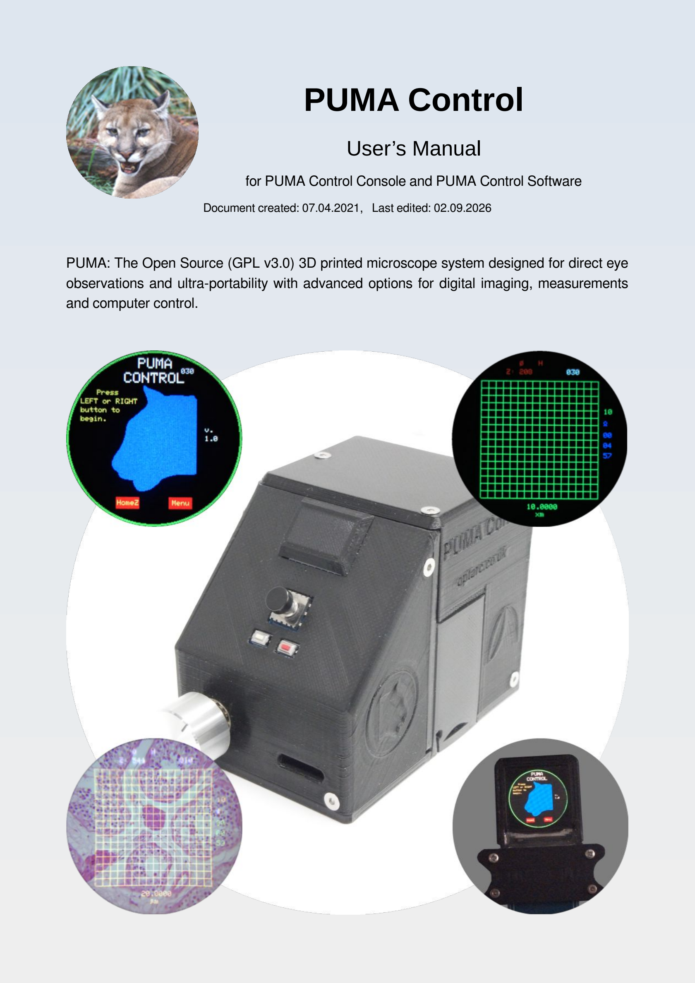
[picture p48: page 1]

for PUMA Control Console and PUMA Control Software

Document created: 07.04.2021, Last edited: 02.09.2026

PUMA: The Open Source (GPL v3.0) 3D printed microscope system designed for direct eye observations and ultra-portability with advanced options for digital imaging, measurements and computer control.

### Contents in Brief

PUMA Control User’s Manual v1.2 | Page 1

### Contents in Detail

PUMA Control User’s Manual v1.2 | Page 2

PUMA Control User’s Manual v1.2 | Page 3

PUMA Control User’s Manual v1.2 | Page 4

PUMA Control User’s Manual v1.2 | Page 5

Keypad actions for the Aperture CM | 73
Index | 74

[This space is intentionally left blank]

PUMA Control User’s Manual v1.2 | Page 6

## Legal Information

### License

Copyright (C) 2021-2026 Dr Paul J. Tadrous
Permission is granted to copy, distribute and/or modify this document under the terms of the GNU Free Documentation License, Version 1.3 or any later version published by the Free Software Foundation; with no Invariant Sections, no Front-Cover Texts, and no Back-Cover Texts. A copy of the license can be found at https://www.gnu.org/licenses/fdl-1.3.html

Limitations of Use The PUMA microscope and its associated systems do not have any certifications or regulatory approvals in any country for use in clinical diagnostics or treatment (human or veterinary). The PUMA microscope and its associated systems are released to be used for research

and educational purposes only. Disclaimer All PUMA project information, including without limitation any CAD file or STL file and all

documentation, advice and instruction (whether provided in video form, audible form, written form or otherwise) is provided ‘as is’ in good faith and is intended to be helpful but comes with no warranty whatsoever. Anyone attempting to build or use a PUMA microscope or other PUMA-related material, accessory, module or derivative is hereby advised that there will be risk involved in 3D

printing, post-print processing, assembly and usage of the resulting structures. This risk includes, without limitation, the risk of personal damage and loss of resources. Dr Paul J. Tadrous, TadPath and OptArc cannot accept any liability for any such loss or damages that may occur. All those who attempt to build or use any aspect of the PUMA project or derivatives thereof do so at their own risk.

PUMA Control User’s Manual v1.2 | Page 7

## Safety Information

Throughout this manual please take heed of warnings given in bold text and highlighted yellow to avoid possible damage to equipment and/or harm to people.
PUMA microscopes and associated systems are not toys. They contain small parts which may come loose such as tiny metal screws and washers and glass components that may splinter or break or otherwise present a choking or sharp object hazard or chemical hazard (for batteries). Please do not let babies or young children play with or use any aspect of a PUMA system without close appropriate adult supervision. Likewise keep PUMA systems away from pets.

## Known Bugs / Limitations

The interaction of the power regulation board with the LED lamp and the power regulator built into the Arduino Nano microcontroller, together with the relatively simple LED current ammeter circuit means that there are some issues with the system that you should be aware of. 1. The power regulator can sometimes loose current regulation. This is known as ‘tripping

the power regulator’ which can cause excessive and damaging current flow to the LED lamp. This is described in more detail on page 16. 2. Spurious ammeter readings. When using batteries, as these wear down and loose voltage and current capabilities the reading on the ammeter can spuriously increase to the point where this causes an over-current alarm even when there is still enough current

draw capability to avoid tripping the power regulator. This issue is further discussed on page 16. For this reason the ammeter reading while on batteries should not be regarded as accurate. With v1.2 of the software the ammeter is turned off by default so you will need to enable it (from the 'Defaults' menu) if you want to use it.

PUMA Control User’s Manual v1.2 | Page 8

## Abbreviations

Some common abbreviations used in this manual are listed below for convenience.

AR | Augmented reality (see page 18)
CM | Control mode (see page 26)
FOV field of view GUI Graphical user interface H&E Haematoxylin and Eosin HUD Heads-up display (see page 18)

IDE Integrated development environment (software) PC Personal computer PCC The PUMA Control console (see page 12) SLM Spatial light modulator (see page 21)

TFT Thin film transistor (liquid crystal display)

PUMA Control User’s Manual v1.2 | Page 9

## Introduction

PUMA is an open source 3D printed high quality microscope system. The name PUMA stands for Portable, Upgradeable, Modular and Affordable – key features of this system. Due to its modular design, a PUMA microscope can come in various configurations from a simple mirror-based microscope that uses no electronics or software at all, to an advanced research microscope with motorised Z-stage and TFT screens for optical image overlay and Fourier optics digital light processing. These electronic peripherals are controlled by an ATMega microprocessor running software to control them. PUMA comes with it’s own standard software known as “PUMA Control”. This manual explains how to use this standard software. Because PUMA is an open source project you may customise this software or write your own interface from scratch. You can even run the PUMA peripherals via a desktop PC or smartphone with your own software interface. This manual does not discuss such alternative control strategies.

PUMA Control was designed to run on an Arduino Nano v.3 microprocessor board programmed using the Arduino IDE v.1.8.15. It uses 30682 bytes of program storage space. The peripherals that PUMA Control is designed to run are those that are contained in or connect to the PUMA Control Console (PCC) – an Arduino-based control box device that

is part of the PUMA open source standard. Instructions on how to build the PCC are provided on the PUMA GitHub pages. It is possible to build a prototype of the PCC on a standard breadboard following the circuit diagram provided on the PUMA GitHub site if you want to try the software but don’t want to go all the way to making the finished portable control console. PUMA Control provides the following input functionality:

- Receives user input from a 5-way joystick keypad. • Monitors the current flowing to the microscope LED lamp. • Monitors the state of the focus mechanism Z limit switch. • Monitors the position of the Z-stage by an open loop system.

PUMA Control provides the following output functionality: • Control of a stepper motor (for the focussing mechanism of the microscope). • Displays the current flowing to the microscope LED lamp on a TFT screen. • Generation and display of a graphical user interface (GUI) on a TFT screen.

PUMA Control User’s Manual v1.2 | Page 10

- Generation and display of various aperture patterns on a TFT screen.
- Generates audible feedback signals to the user via a piezo buzzer.
This manual describes how to interpret and control these features so you can use the advanced features of the PUMA microscope.
This manual pertains to PUMA Control v1.2

## Hardware

PUMA Control is all about controlling certain hardware so you can’t understand how to use it without knowing something about that hardware. This chapter familiarises you with the input and output devices that you will be using with the PUMA Control software. The terminology and abbreviations introduced here will be required to fully understand the rest of the manual. Optional add-ons and updated features like the 10 cm monitor module for the PCC will not be discussed here.

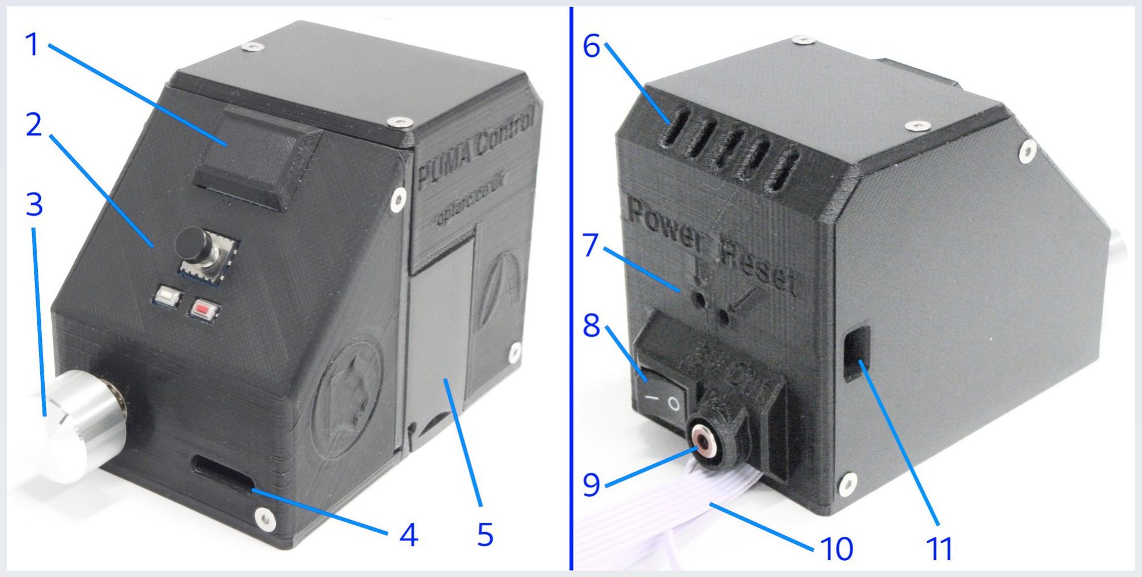
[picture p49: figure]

Figure 1. The PUMA Control Console (PCC) v1.0. Left: Front and right aspect. Right: Back and left aspect. Labels: 1. Mouse upgrade port (this is a window designed to allow an external mouse to be used instead of the integrated joystick keypad. The mouse device has to be a special PUMA mouse designed for Arduino – not a standard USB or PS2 mouse). 2. Joystick keypad. 3. Lamp brightness potentiometer (Bourns 10-turn linear type). 4. Window to allow viewing of the Z-motor control board status indicator LEDs., 5. Battery compartment slide-on cover. 6. Passive cooling vents. 7. Window to allow viewing of the Arduino Nano power indicator LED and to allow access to the reset button. 8. Power On/Off switch. 9. Power output to the microscope LED lamp. 10. Cables to connect to external peripherals (Z-motor, Z limit switch and TFT screen of either the SLM or the AR projector or the optional 10 cm monitor module for the PCC). 11. Access to the USB port of the Arduino Nano.

PUMA Control User’s Manual v1.2 | Page 11

### The PUMA Control Console (PCC)

The PCC is the battery-operated portable control box that houses the Arduino Nano microprocessor which runs the PUMA Control software. It has the following features (see figure 1):
- It runs from two 9v batteries (type 6LR61) or, alternatively from an external power source with the following characteristics:
- it must be able to provide at least 1 Amp of current,
- it must have a Voltage anywhere in the range of 7 to 12 Volts, ◦ it must be able to connect via the standard 6LR61-type connector. Such an external power source may be an external battery pack (e.g. holding 8x AA batteries) or a regulated mains power adapter. • It has an internal piezo buzzer to produce audible feedback signals for the user.
- It contains a ULN2003-based stepper motor controller board with 4 LED indicators visible from a window in the front of the casing. • It has a 10-turn Bourns potentiometer on the front connected to an internal constant current power regulator board to provide some manual user-control over the current output to the microscope lamp. It is advisable to keep this

potentiometer turned down (to its low brightness setting) or at least to its mid-way position whenever the unit is switched off (and prior to switching it on) because otherwise the PCC may draw a large inrush current when switched on and this could result in a transient voltage drop at the input of the internal power regulator that could ‘trip’ requiring immediate corrective action (see ‘Tripping the power regulator – Immediate Action Required’) below.

- It has a 5-way joystick plus 2-button keypad on the front panel as a manual user interface. More detail on the ways you can provide input from this keypad will be given below. • It has a phono socket on the back which is a 5 V power output port for the

microscope LED lamp. Only connect the microscope LED lamp to this phono
| | socket – it is NOT a video or audio port. Attempting to connect any video
or audio equipment to this | phono | socket | could permanently damage the
audio or video equipment.
- It has three ribbon cables coming out of the back with JST XH connectors on them. These are for connecting to the Z-motor (the 5-pin connector), the Z-limit switch (the 4-pin connector) and an ST7789 miniature TFT screen (the 7-pin connector).
PUMA Control User’s Manual v1.2 | Page 12

ST7789 TFT screens come several forms: some work from a 5 Volt supply in both logic and power supply, some may work with either 5V or 3V and others that can
only work from 3 Volts. | Only the 5 Volt compatible versions | of these mini
TFT screens can be used with the PCC. If you attempt to use a 3 Volt-only TFT display you will instantly and permanently destroy the display. The PUMA open hardware standard specifies that only 5 volt-compatible versions of the ST7789 TFT screen may be used when constructing the augmented reality (AR) projector and the spatial light modulator (SLM).
Note that all text and numbers displayed via the PCC on a TFT screen will be in mirror-writing. This is because the optics of the scope optically ‘flip’ the display image before it is presented to the user. A single PCC can only connect to one TFT device at a time so either the AR projector or the SLM can be used – not both simultaneously. You would need two PUMA Control consoles to run both these modules simultaneously. If you require a GUI but don’t want to build (or otherwise don’t have) either an SLM module or AR projector then you can connect a bare 5

Volt compatible ST7789 screen to the PCC but you will see the GUI in mirror-flipped form. You can use a mirror to correct this. If you do this take care to ensure the connections are the correct way round because ST7789 modules usually do not come with a JST connector attached. For bare pins connections the ‘Gnd’ (ground) pin of the TFT module connects to pin 1 of the JST connector coming from the PCC (pin 1 is the pin adjacent to the ‘V’-shaped notch in the short side lip

of the casing of the JST XH female connector and this notch can be seen in figure 2). For connecting to the AR projector unit, the correct polarity is shown in figure 2. Note that these TFT screens are NOT ‘hot swappable’ i.e. you must have the screen device of your choice connected prior to switching on the PCC so the screen electronics can ‘boot up / sync’ correctly. If you need to change the TFT

screen you must switch off the PCC first then disconnect the current screen, connect your new screen and then switch on. Attempting to change screens while the PCC is powered up will likely result in the newly attached screen not working (although this can usually be remedied by switching the PCC off then on again). You may find during normal use that the GUI on your connected TFT screen freezes and becomes unresponsive. This happens if the connection between the

screen and PCC is disrupted e.g. by moving a cable that has a tenuous connection. The only way to fix this is to switch the PCC off then on again – and ensure the connection is robust (possibly strengthened by taping the connector ends together) to avoid repeat disruption. • A USB port to allow connection of the PCC to a computer for the purposes of programming the PCC’s internal Arduino Nano, downloading data from the Nano

PUMA Control User’s Manual v1.2 | Page 13

to an external device or interfacing the unit to an external computer. See the section on ‘Programming the PCC’ below for more details on how to use this port including important safety information.

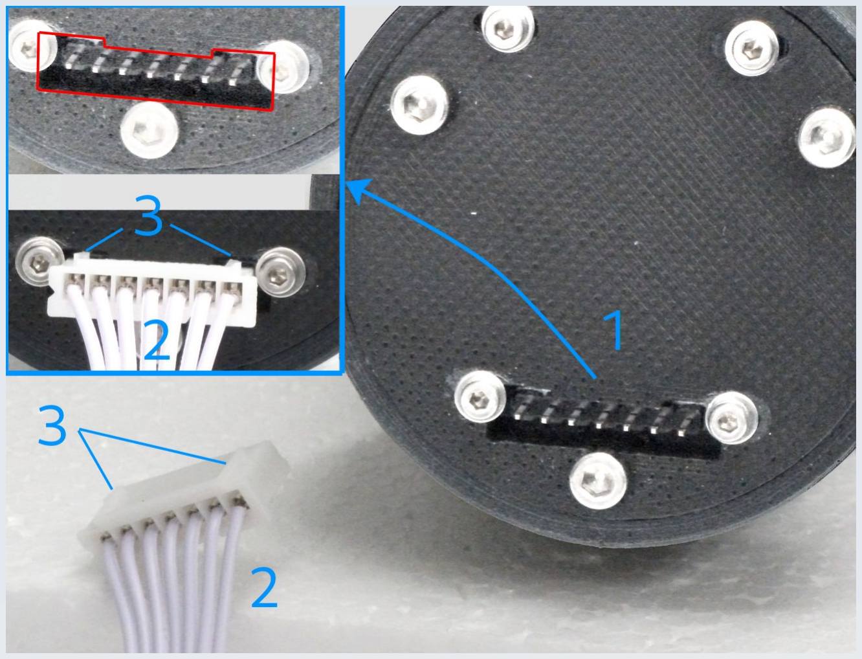
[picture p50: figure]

Figure 2. Polarity of connection to AR Projector. Main figure: Back of AR Projector (see figure 4 for the whole AR Projector). Inset shows the connector with its outline highlighted in red (top) and the connector in place (bottom). The JST connector has two raised lugs on one surface and these go into the recesses provided in the cut-out for the connecting pins at the back of the AR projector as shown. 1. Cut-out and pins at the back of the AR projector. 2. 7-pin JST XH connector coming from the PCC. 3. Lugs on the 7-pin JST

XH connector. Using an external power source To use an external power source with the PCC (either an external battery pack or a mains adaptor) you must do the following (figure 3): 1. Switch off the PCC and open the battery compartment

2. Remove the two 9V batteries from inside (completely disconnect both of them) 3. Put the upper battery connector lead back inside the battery compartment but externalise the lower battery connector lead.
PUMA Control User’s Manual v1.2 | Page 14

4. Ensure that the externalised battery connector lead cable is in the ‘V’-shaped recess in the case then slide the battery compartment cover in almost all the way (but not fully).
5. Thread the externalised battery connector cable into the slot in the battery compartment cover then close the cover all the way.
You now have an externalised 6LR61-type connector which you can use to connect an external power source, including a regulated mains adapter. Ensure that the connected source provides power in the range of 7 to 12 Volts (any higher will damage the Arduino
| Nano, any lower and some components will not work properly or at all). The external power supply must be able to supply at least 1 Amp of current or the PCC will not function correctly and may give unpredictable / erratic behaviour. Also, if current is insufficient, it can result in a voltage drop at the input of the internal power regulator of the PCC and this can cause it to ‘trip’ requiring immediate corrective action (see ‘Tripping the power regulator – Immediate Action Required’, below).
| Important: Always remove both internal batteries as described above when using an
battery connected when using an | external power source or the internal battery

external power source (whether battery pack or mains adaptor). Never leave an internal

may | leak corrosive toxic chemicals or | explode. This is because both battery
connectors are directly connected to each other and you will effectively be ‘re-charging’ the connected internal battery using the external battery or power source and this re-charging will be uncontrolled.
PUMA Control User’s Manual v1.2 | Page 15

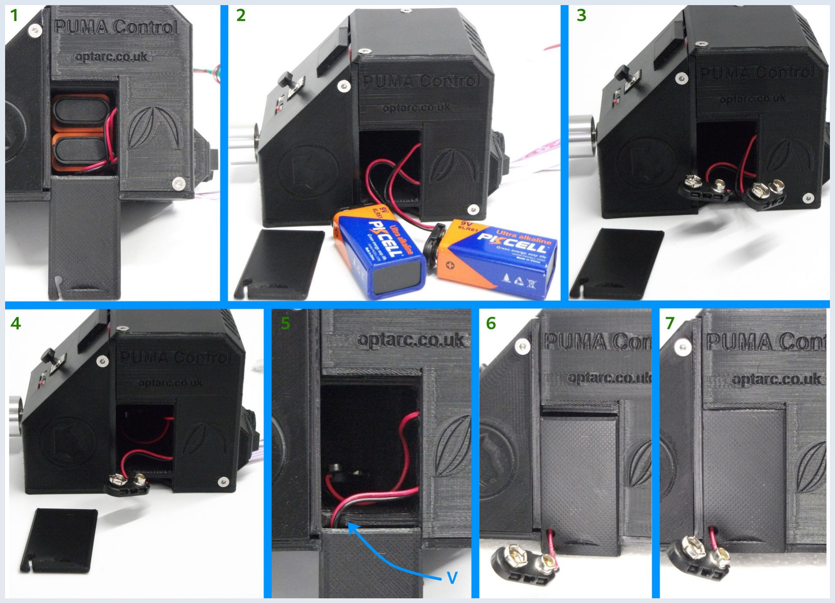
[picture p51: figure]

Figure 3. Externalising the power connector on the PCC. 1. Open the battery compartment. 2. Remove both batteries. 3. Disconnect both batteries. 4. Put the top battery connector back in the battery compartment. 5. Leave the lower connector out of the case and begin to slide the battery compartment cover back on making sure the externalised lead is in the ‘V’-shaped groove in the casing (marked ‘V’ here). 6. Continue to slide the cover on and insert the externalised connector lead into the slot in the battery compartment cover. 7. Completely insert the battery compartment cover. Tripping the power regulator – Immediate Action Required

Any cause of low voltage at the input to the internal power regulator of the PCC can cause the regulator to ‘trip’. This means the regulator no longer regulates the output current properly which, in turn, could overload the LED bulb. This will usually be accompanied by an audible warning alarm of the piezo buzzer and a visual warning in the TFT display of the augmented reality projector (the current value display will turn red and flash). It is possible that such warnings may fail to occur and in that case you will notice the fault by

noticing that the LED bulb appears much brighter than it normally does. If this happens you should remedy the situation quickly by simply switching off the PCC, turning down the brightness potentiometer (turn it clockwise to do this) and then switch on

again. Failure to act quickly in such a situation could result in drastically reducing your LED lamp life or cause it to blow altogether.

PUMA Control User’s Manual v1.2 | Page 16

Situations that can result in tripping the power regulator are any which result in a low voltage at the input of the regulator. This is usually due to a low current power supply situation. This can occur either if your batteries are running low or you use an external mains supply that cannot provide over 1 Amp of current or you attempt to use the unit on only one 9V battery instead of 2. When using a power supply that is failing or has a low current rating, the ‘trip’ may not occur immediately when you switch on. Instead it may only occur when you try to move the Z motor or when you turn up the brightness with the potentiometer – then you may notice a trip as a sudden ‘jump’ in the brightness of the microscope LED lamp (if the above mentioned warning signals don’t engage).
It is also possible that a false alarm high current signal may be generated as batteries wear low. This is due to the simple nature of the ammeter circuit and is a known limitation of the current software / hardware PUMA Control system. If this becomes an irritation you can disable the ammeter from the ‘Defaults’ menu but then you would loose this audible visual warning for when a real over-current situation occurs. If you use the PCC with the brightness potentiometer turned down this should not be a practical issue but it can be a

problem if you use the PCC with the brightness potentiometer set at or near its maximum brightness setting. Use this ammeter disable option with caution. Programming the PCC The PCC has a USB port to enable the internal Arduino Nano to be interfaced to another

device. This ‘other device’ will usually be a PC which is used to update or upgrade the software on the Nano or to read data from it.

IMPORTANT: Before connecting any device to the USB port of the PCC, ensure that the PCC is switched OFF from its main power switch and physically remove the LED lamp connector from the 5V output phono socket. Do not attempt to use
the stage motor or plug in the LED | lamp | while the | PCC | is connected to an
external device via its USB port. The only exception to this rule is if you have set up your own custom interface system with sufficient power distribution to handle the attached devices. Failure to heed this advice could permanently damage your attached PC (or whatever device the USB cable is attached to) because the devices in the PCC may attempt to draw too much current from the USB-connected device.
Once the PCC is switched off and microscope lamp disconnected from the phono socket at the back of the PCC, connect the PCC to the device used for programming (such as a PC running the Arduino IDE) with a standard IDE cable. You can then upload the new software as per the instructions for using the Arduino IDE. Once complete, remove the USB cable from the PCC, reconnect your lamp and switch on the PCC to use the new software.
PUMA Control User’s Manual v1.2 | Page 17

### The augmented reality (AR) projector and heads-up display (HUD)

PUMA provides for a digital overlay – called a ‘heads-up display’ (HUD) – of interactive information that is superimposed onto the live optical image of the specimen via a projector attachment module known as the augmented reality (AR) projector (figure 4).

Figure 4. The AR Projector module
and the HUD. Main image shows the
AR Projector (highlighted in the blue
box) attached to a PUMA microscope. The inset lower right shows an example of the HUD as seen through the ocular lens with graphics (a grid and some numbers and symbols) superimposed on the live optical microscope image. In the

rest of this manual, the HUD will be illustrated without an underlying microscope image for clarity of illustration except where demonstration images are needed to highlight certain features.

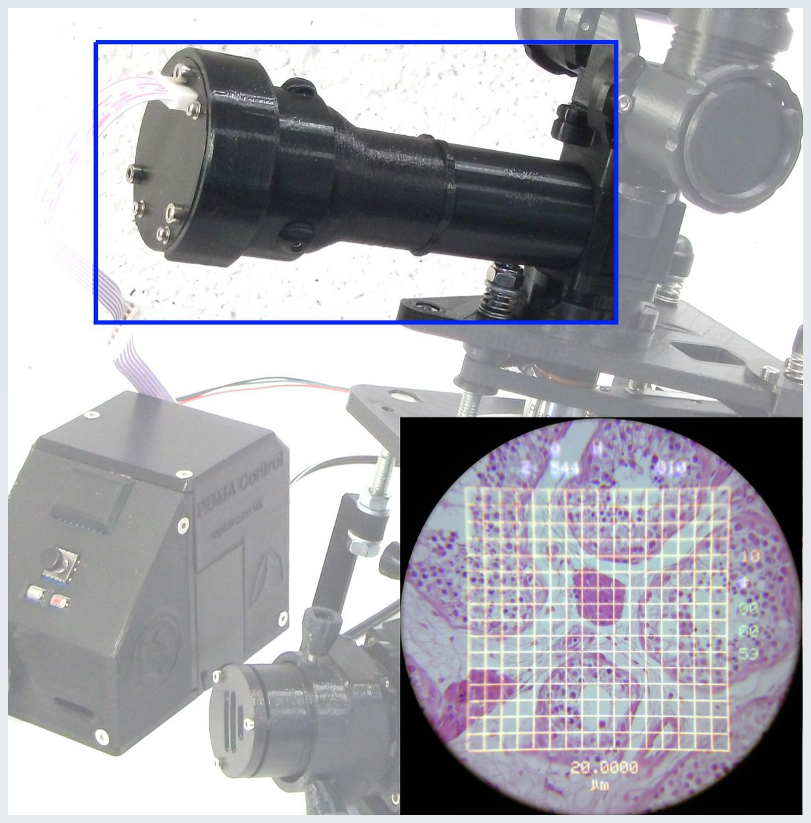
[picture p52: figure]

The larger end of the AR projector contains an ST7789 colour TFT display screen which connects to and is driven by the PCC. The rest of the AR projector consists in lenses that project the image of this TFT display onto the back focal plane of the ocular lens – the same plane that the objective lens of the microscope projects the image of the specimen on the stage. In this way the two images are superimposed to the viewer looking down the ocular lens(es) of the microscope. The panels of the HUD

The details of what information when discussing the various modes of operation of the PCC (known as ‘control modes’) but, in general, the HUD divides the round field of view (FOV) of the ocular lens into 5 regions, a central square region and 4 peripheral segment display panels outside the central square (figure 5). The peripheral green ring indicates the limits of the field of view of the HUD and is displayed on the boot up screen and in menu mode (only). It is intended | is displayed will be discussed throughout this manual
PUMA Control User’s Manual v1.2 | Page 18

to be used as a guide to the user when they set up the AR Projector so as to help centre the HUD in the field of view and ensure optimal magnification is achieved when adjusting the AR projector. Optimal magnification is achieved when the innermost part of the peripheral green ring is just visible all around the field of view when looking down the ocular lens.

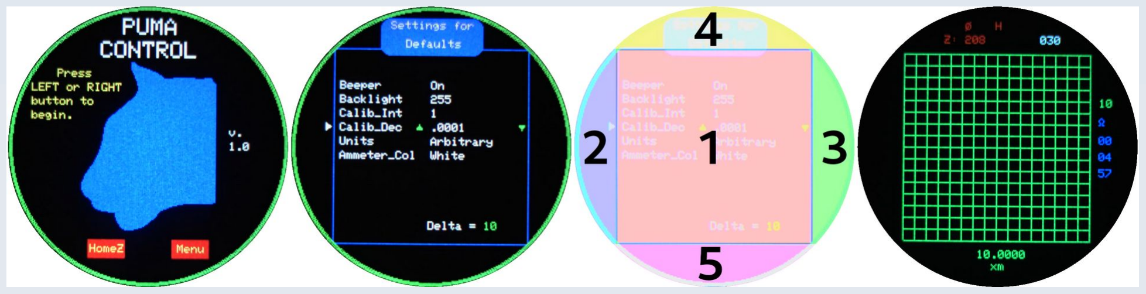
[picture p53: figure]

Figure 5. The HUD. From left to right: The boot-up screen, an example menu screen, the 5 regions of the HUD, an example of user-customised colours for different information displays. For many of these display areas the user may select the colour of the text and graphics via a setting in the GUI menu as will be described in more detail later – the default is white. If the colour ‘Black’ is selected then this will effectively make that part of the display

invisible. In fact, that is the reason why ‘black’ is offered as an option – to give the user the ability to selectively ‘switch off’ specific aspects of the HUD.

PUMA Control User’s Manual v1.2 | Page 19

The 5 main display regions are:
1. A central square area whose corners reach the limits of a 20 mm FOV
2. A left panel outside the central square area
3. A right panel outside the central square area
4. A top panel outside the central square area
5. A bottom panel outside the central square area
The following gives a summary of what information is shown in each region. Not all the information items for a given region will be shown all the time. The amount of information shown depends on user settings and on what control mode the user is currently in. Various symbols are briefly mentioned but not fully explained. Such detail will be given elsewhere in the chapters of this manual when the various control modes are described. The central square area

This can show: • Any grid, cross-hairs or scale bar patterns • The interactive cursor / pointer* • Any marker symbols laid down by the user*

- Lines drawn for the purpose of measurement* • The menu options when in menu mode * Items marked with an asterisk can actually be drawn / displayed anywhere on the TFT screen, including in any of the peripheral segment panels and even outside the round FOV of the ocular.

The left panel This can show: • The menu item selection arrowhead when in menu mode.

The right panel This can show (from top to bottom): • An integer representing the number of HUD pixels between divisions of any grid or cross-hair pattern or the length (in HUD pixels) of any scale bar. This number only shows when in Graticule control mode.

PUMA Control User’s Manual v1.2 | Page 20

- The symbol for Z-motor control mode ( ) or Timer control mode ( ) when either of those modes are the currently active mode.
- The hours on the timer
- The minutes on the timer
- The seconds on the timer

The top panel

This has two lines of information. The upper line can show (from left to right): • An icon representing the Z-motor coil energisation state ( , or ). • The coarse focus speed symbol ( ). • The ‘stage is homed’ symbol (H).

- The ‘sweep mode’ symbol ( ). The lower line can show (from left to right): • The current position of the Z stage as the characters “Z: “ followed by an integer. • A triplet of integer digits representing the lamp current.

The top panel also shows the menu level heading when in menu mode. The bottom panel This has two lines of information. The upper line can show:

- A number (integer or floating point) representing the result of a measurement or the calibrated distance between divisions of a grid or cross-hair pattern or the calibrated length of a scale bar. The lower line can show: • The units of a measurement.

The Spatial Light Modulator (SLM) In traditional microscopes the condenser’s aperture, and the aperture of the field stop in Köhler systems, are regulated by a mechanical iris that presents an essentially round stop

PUMA Control User’s Manual v1.2 | Page 21

the diameter of which can be varied by turning a dial. This very limited system of aperture control suffices for most routine observations. Some advanced scopes have the ability to block the central part of the condenser’s aperture with a round spot of various diameters to allow for dark ground microscopy.
PUMA takes a different and more flexible approach. The PUMA systems use a filter-like tray containing an aperture pattern which is inserted into a slot at the base of the condenser (to control the condenser illumination) or a slot just beyond the lower collector to control the illuminated field of light.
This may at first seem like a retrograde step – a physical filter can only have a fixed pattern and can’t be adjusted with a rotary control like an iris diaphragm. However, this is not so. The filter used with a PUMA scope can contain very complex patterns – even arbitrary shapes, so is not limited to a simple circular hole. Also, the PUMA aperture filter can have shades of grey or colour transparency so it not limited to all-or-nothing transmission like an iris diaphragm. While these complex pattern can be printed onto a

fixed glass filter, a much more flexible approach is to use a transparent colour TFT computer screen as the filter to allow dynamic computational control over the aperture function. Such a dynamic light modulation system is known as a ‘spatial light modulator’ (SLM) and figure 6 shows an example of a manual filter and of the TFT-based SLM.

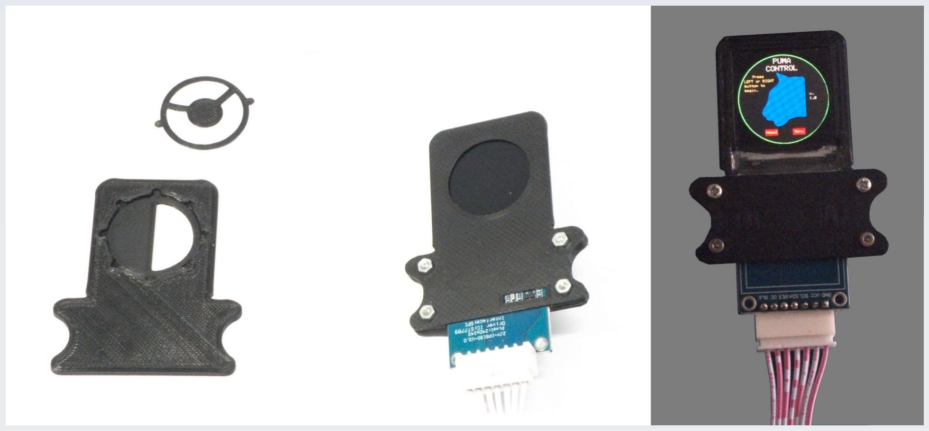
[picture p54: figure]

Figure 6. A manual aperture filter (left) and the PUMA SLM filter (middle – seen from the bottom aspect and switched off, right – seen from the top aspect and switched on showing the boot up screen). The Manual filter takes up to two filter discs simultaneously to built up complex patterns. It can also accept a round coverslip glass disc on which may be printed even more complex patterns with colour and semi-transparency but it will be a fixed aperture either way. The SLM uses a TFT screen so it can generate active and changing complex apertures. Both fit into the same filter slot so they are interchangeable. The picture on

PUMA Control User’s Manual v1.2 | Page 22

the far right shows the SLM in front of a bright light which is how the image is made visible – there is no intrinsic backlight or reflective panel in the SLM.

The apertures presented on the SLM can be controlled by the PCC but the amount of control allowed in the default PUMA Control software is very limited compared to the full potential of what can be achieved with this device. The SLM is an advanced feature of the PUMA microscope and it is anticipated that those wishing to use it will write their own interface software to achieve the type of transmission functions they require for their
| specific purposes. The Z-motor and Z-limit switch The stage of a PUMA microscope can be fitted with a stepper motor to enable motorised focus control. The type of motor used in the current PUMA standard is a 28BYJ48 motor. This motor comes in two voltage types: 12V and 5V. If you are using a 9V (or lower) power
| supply then the 5V version of the motor should be used because the 12V version, if run at these low voltages, will not provide enough torque to turn the gears reliably at all speeds

voltage power supply is used, such as a 12V battery pack or power adaptor, then you MUST use the 12V version of the motor because at these high voltages the 5V version of the motor will severely and dangerously overheat with risk of

without stalling (it will be more likely to stall | at faster speeds). However, | if a higher

burns and also melting of the plastic coupling gear rendering it useless. As a safety feature and also to allow open loop monitoring of the Z position of the stage at any time, an end stop limit switch is also part of the PUMA stage motorisation kit. These apparatus can be seen in figure 7.

Figure 7. The PUMA stage fitted with a stepper motor
(M) and limit switch (L) to allow motorised control over
focus. The PCC to which they are connected is shown at the bottom of the figure.

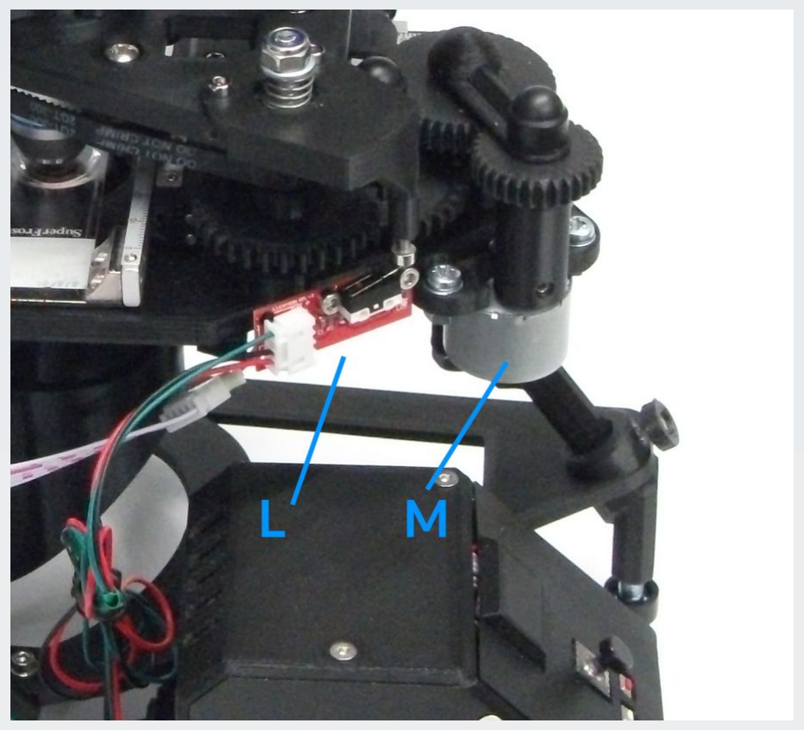
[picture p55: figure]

PUMA Control User’s Manual v1.2 | Page 23

The PCC is designed to connect to and drive the stage motor and to monitor the limit switch state. Details will be provided in the dedicated section of this manual.

### User input via the joystick keypad

The joystick keypad on the front panel of the PCC was introduced above and illustrated in figure 1. This section gives detailed information on the types of input actions (sometimes called ‘key actions’) a user can make with this keypad and how these input actions are referred to in the rest of this user manual.

The joystick The joystick has 5 primary activation actions. The user can also use simultaneous combinations of these 5 actions to effect additional signals to the PCC. The joystick can be moved in any of the 4 primary directions (up, down, left, right) and can also be clicked directly inwards (hence ‘5-way’). It can also be moved in the 4 diagonal

directions e.g. you can move it up and left diagonally and it will activate both the ‘up’ and ‘left’ signals simultaneously – the PUMA control software can detect and respond to such dual simultaneous signals. However, these diagonal joystick movements are only used for moving the cursor around the screen in the ‘Pointer’ control mode so are not given specific abbreviations in the scheme described below.

The left and right (set and reset) buttons The two separate buttons below the joystick are called ‘Set’ for the left button (the white button in figure 1) and ‘Reset’ for the right button (the red button in figure 1). This set/reset terminology is used in this manual instead of left/right to make it clear we are talking about the these buttons and not joystick direction movements. However, the written message on the boot up screen of PUMA Control says ‘Press LEFT or RIGHT button to begin’ (using

the word ‘button’ to distinguish them from joystick actions). Note that the PCC Arduino can be physically reset (a hard reset) using its own reset button i.e. the reset button that is on the Arduino Nano board inside the PCC case. This can be accessed, e.g. with a match stick, via the hole in the back of the PCC case labelled ‘Reset’ (see figure 1, right). This internal ‘Reset’ button has nothing to do

with the ‘Reset’ / right button on the front keypad and for the rest of this manual whenever a ‘Reset’ button or reset action is referred to it only refers to the right button on the joystick keypad on the front panel of the PCC.

PUMA Control User’s Manual v1.2 | Page 24

How to issue a combination key action signal

The ‘Set’ button can be clicked on its own or in combination with some other button. In this section ‘some other button’ includes a joystick action as well as the ‘Reset’ button. The PCC can detect such combination presses and act accordingly. However a combination press must be done in a certain way to be properly recognised.
The correct way to do a combination press is to press the ‘Set’ button first, then press the other button while the ‘Set’ button remains depressed. You then release both buttons simultaneously. The exact order of release is not important but it should be approximately simultaneous because if you linger on one or other button then that will register as a second, single, button press. In order for the PCC to distinguish between a ‘Set’ only press and a ‘Set’ + ‘Other’ combination press, the program waits for a maximum of 500 ms when it detects the ‘Set’ button first being pressed to see if a second button is going to be pressed as well. If no other button is pressed in this half-second interval then the PCC interprets the action as a

solitary ‘Set’ press and acts accordingly. So you must press the other button within half a second of first depressing the ‘Set’ button to register a combination press signal. Note that there is no valid combination signal that comes from clicking any button first except the ‘Set’ button with the sole exception of the diagonal joystick movements in Pointer control mode described above.

List of allowed input signals from the joystick keypad In the rest of this manual the following symbolism / terminology is used to mean the following actions: JS_UP : Move the joystick up

JS_DOWN : Move the joystick down JS_LEFT : Move the joystick left JS_RIGHT : Move the joystick right JS_MID : Click the joystick in (towards the control panel) SET_BTN :

SET : Click the Set button on its own SETRST : Click the Set button in combination with the Reset button SETDOWN : Click the Set button in combination with JS_DOWN SETUP : Click the Set button in combination with JS_UP

PUMA Control User’s Manual v1.2 | Page 25

SETMID | : Click the Set button in combination with JS_MID
SETLEFT | : Click the Set button in combination with JS_LEFT
SETRIGHT : Click the Set button in combination with JS_RIGHT RST_BTN : Click the Reset button

As indicated earlier, there is no valid ‘RSTSET’ action – i.e. there is no valid combination signal that arises from pressing the ‘Reset’ button first and then the ‘Set’ button while the ‘Reset’ button is still pressed. If you try this you will just trigger the action that occurs when pressing the ‘Reset’ button on its own. Likewise there is no valid combination signal that arises by pressing ‘Reset’ first in combination with any joystick action. Although such combinations are technically possible, the PUMA Control software is not programmed to respond to them and will react as if ‘Reset’ were pressed on its own. Using the above system of single and combined activations, including the diagonal

joystick movements for the pointer, the PCC can use this very limited joystick keypad to recognise 17 different input signals from the user. Control modes

PUMA Control allows various functional aspects of the system to be controlled by the joystick keypad such as focussing the motor, making measurements, etc. Because the single joystick keypad is too limited an input device to allow simultaneous control of all these many features at once, the user selects which functional aspect of the system they want to work with via a menu and then the Joystick keypad will have particular input functions suited to controlling that aspect of the system. Each of these These ‘functional

aspects of the system’ is called a ‘control mode’ (CM). There are a total of 6 control modes which will be described in detail in their dedicated sections in this manual. The control modes are: 1. Z-Motor : Allows control over the stage focussing motor with various options. Focussing is such a basic aspect of using a microscope that the Z-Motor control

mode is the default control mode after boot up and there is also a shortcut key action that allows the user to quickly toggle between any other control mode and the Z-Motor control mode without having to go through the main menu. So a user can easily focus the scope while working, say, with a graticule in Graticule control mode without having to completely leave the graticule mode or remove the graticule from the main display area.

PUMA Control User’s Manual v1.2 | Page 26

2. Pointer : This allows control of an interactive pointer / cursor on the HUD which can be used for pointing, marking objects, counting objects and drawing lines to be measured in length and angle.
3. Timer : Set and use a count-up or count-down timer. The time will continue to count time even when you move to a different control mode so it can be used simultaneously with other modes. Selected quick link shortcuts are also provided to this mode but not as extensively as with the Z-Motor control mode shortcut. A running timer is the only display which persists when the user switches to the menu. 4. Graticule : This allows you to superimpose a range of graticules, cross-hairs and scale bars on the field of view via the HUD. Each graticule can be varied in scale and colour. 5. Plain : This sets a completely plain field of view on the HUD which can be varied in colour. Use this for illumination effects. When used with the SLM this can act as a

programmable colour filter to colour the illumination of the scope. 6. Aperture : This allows apertures of various sizes and colours to be generated for use with the SLM. You can cycle between a plain bright field circular aperture (and open and close it in graded steps like an iris), a half-field Schlieren aperture for phase contrast (you can rotate it by 90 degrees as desired) and a central stop

aperture of various sizes for dark field microscopy. You can also superimpose the dark field central spot onto either of the two preceding patterns. By varying the colours of the different components you can create Rheinberg filter illumination effects

Software Installation Notes PUMA Control is an Arduino sketch (.ino file) intended for use on the Arduino Nano v. 3.0 to be compiled and installed using the Arduino IDE v. 1.8.15 or compatible. It uses a modified version of the Adafruit GFX library where the default font has been customised to draw mirror writing and also to draw custom graphics characters. This

custom version is named GFXM and is found in the ‘libraries’ folder of the PUMA_Control repository in the folder called GFXM_Library. Ensure that the folder ‘GFXM_Library‘ is placed in your Arduino libraries folder as shown below. This customised library is kept as a separate re-named library so that it does not get overwritten each time the standard Adafruit graphics library is updated. This GFXM_Library folder also contains a

PUMA Control User’s Manual v1.2 | Page 27

customised version of the standard Arduino library Print.cpp file which ensures that all writing is right to left - i.e. mirrored.
PUMA Control also uses a slightly modified version of Pawel A. Hernik's "Arduino_ST7789_Fast" library which is called 'ST7789_FastM'. This should be placed in your Arduino libraries folder as shown below.
Make sure you have these modified libraries (all of which are included in the PUMA GitHub distribution) in the appropriate folder for your version of the Arduino IDE to use when compiling and uploading PUMA Control to your Arduino Nano (inside the PCC). For example, on a Linux OS you may have the following directory structure: ~/Arduino/libraries/ST7789_FastM
~/Arduino/libraries/GFXM_Library ~/Arduino/MySketches/PUMA_Control/PUMA_Control.ino
PUMA Control User’s Manual v1.2 | Page 28

## The Meaning of Audible Signals

PUMA Control has two sources of feedback for the user: Visual feedback via the TFT display (of either the SLM or the AR Projector HUD or the optional PCC 10 cm monitor) and audio feedback via the piezo buzzer in the PCC.
There are 6 characteristic audio feedback signals have been carefully designed to be as helpful and meaningful as possible because not everyone will be using the PCC with a TFT screen device (e.g. the PCC may be used to control of the Z-motor and lamp brightness only). This chapter describe these signals and what they mean. Each characteristic signal is given a name. These are the names of the audible feedback signals: SILENCE

ACKNOWLEDGED PROMPT FORBIDDEN TRILL

TIMEOUT LAMPHOT In the following descriptions a ‘key action’ or ‘key activation’ refers to any of the button or joystick actions using the joystick keypad of the PCC.

SILENCE A special case override to the ACKNOWLEDGED signal for certain key actions. Specifically when moving the pointer around or moving focus up or down with the joystick, the ACKNOWLEDGED signal is replaced by SILENCE i.e. no sound and no delay in the loop function that looks for key actions.

ACKNOWLEDGED This is a single beep. It acknowledges a key action. The total amount of delay introduced by any buzzer signal must be at least 200 ms (regardless of how long the buzzer sounds for) in order to minimise the risk of inadvertent double-key activation.

PUMA Control User’s Manual v1.2 | Page 29

## PROMPT

This is a double beep. It brings the user's attention to a normal state or indicates that they are being prompted to make a decision. For example when boot up is complete (so the system is ready to accept key commands) or when a confirmation question requiring a response is being asked by the system (e.g. 'Do you really want to delete all data points?'). The PROMPT signal is the PCC saying ‘it’s over to you. Your move.’

## FORBIDDEN

This is a triple fast beep. It brings the user's attention to an inability to perform the desired action (due, e.g. to a limit having been reached or a condition not met). For example this will occur if a user tries to access motor functions if the stage has not been homed or if a min/max motion limit is reached. It will also sound if you try to undo a drawing mark when there are no more marks left to undo, etc.

TRILL This is essentially a very fast triple beep. It means the system is entering silent mode (i.e. the mute setting). This is the only meaning for this signal. TIMEOUT

This is 6 beeps in a row. It means the end of a countdown has been reached (i.e. the audible signal for the timer). This will override the mute setting if the user has requested an audible signal for a count-down (either alone or in combination with a visible signal). LAMPHOT

This is 4 beeps in a row. It means the lamp is being over-driven with too much current and may be destroyed if immediate action is not taken. This will override the user's mute preference because it is a safety warning. This signal will repeat itself continually until the current is reduced to safe limits. There will be a brief gap between repeats so the user can distinguish it is 4 beeps recurring and not a continuous train of beeps.

Notes Sometimes a PROMPT or FORBIDDEN signal will be immediately followed by the single beep of ACKNOWLEDGED, at other times it won't. There will be a brief pause between signals. The user may need to get familiar with these signals to appreciate this.

PUMA Control User’s Manual v1.2 | Page 30

## The Boot Up Screen

With all hardware properly connected and lamp brightness potentiometer turned down (or at least to its half way point) switch on the power button on the PCC.

Figure 8. The Boot up screen. The written message says ‘Press LEFT or RIGHT button.’ (using the word ‘button’ to distinguish them from joystick actions). However, this manual uses the terms ‘Set’ for the left button and ‘Reset’ for the right button. Note that the two buttons are
| | | represented as red rectangles at the bottom of the boot up screen with their respective actions written on them in yellow text. The number just to the right of the ‘PUMA CONTROL’ title is the ammeter reading – in this case ‘080’ indicating that the current drawn by the microscope LED lamp is 80 mA. If no lamp is connected to the PCC this number may not appear (as was the case in figure 5,

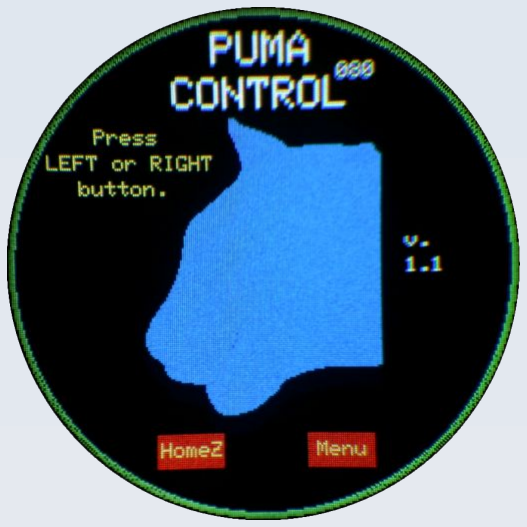
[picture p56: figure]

After a few seconds the PROMPT audio signal occurs (see page 30) and the boot up screen appears to let you know the program is ready to use (figure 8). The microscope lamp will turn on immediately – there will be no delay and no need to wait for the boot up | | | left). The software version is shown mid-right. Note: The image is for v.1.1 of the software. For v.1.2 the ammeter is disabled by default so you will not see the current at boot.
because the lamp is powered independently of the software. In the boot up screen you have 3 options: | 1. Press the left button (i.e. ‘SET’) motor must be homed before you can use it but you are free to use the rest of the software functions without homing the motor - e.g. if you do not have a motorised | | to initiate a Z-Homing procedure (the Z-stage
| stage or if you just want to use control mode for details of the Z-homing procedure. 2. Press the right button (i.e. ‘RST_BTN’) to take you to the main menu to select a control mode. 3. Press the central joystick button (i.e. ‘JS_MID’ ) to mute the device. You will hear the TRILL signal indicating that the device has gone into mute. Press the central | manual focus). See the section on the Z-Motor
Performing any other key action in the boot up screen will have no effect. You will not see the boot up screen again until you next switch the PCC on. | joystick button again to undo mute (there will be no audible signal for this – not even the key press ACKNOWLEDGED beep – because the system was in mute when you pressed the JS_MID to re-enable the audio).
PUMA Control User’s Manual v1.2 | Page 31

## The Menu

The menu allows you to select the mode of operation (called the ‘control mode’) and set various preferences and settings.
The menu has a maximum of two levels: The main menu and one submenu for each control mode and for some global default settings.
Each menu has a number of ‘items’ you can select. Each item has a ‘value’ you can change. If a value of an item is the string ‘[…]’ then this means that if you select that item you will be taken into a submenu. General navigation You enter the main menu from any control mode by clicking the ‘Reset’ button.

You navigate the menu with the joystick. If you have entered a sub-menu, use the ‘Reset’ button to take you back to the main menu. If you are already in the main menu the ‘Reset’ button will take you out of menu mode and

into the currently active control mode. Item select mode When you first enter a menu you will be in ‘item select mode’ which enables you to select which menu item to work on (figure 9). This mode is recognised by the fact that there is a white arrowhead on the left HUD panel (pointing to a menu item) but NO green arrow

heads surrounding the value of any menu item. In ‘item select mode’ you move the arrow head up or down with the joystick till it points to the menu item you want to activate or edit. The arrow cycles around i.e. when it is at the top item, if you move the joystick upwards, the arrow will appear at the bottom-most item and vice versa.

When you position the arrowhead at the menu item you want to work on perform a JS_RIGHT action to select the value of that menu item for editing. If the item value shows as ‘[…]’ then selecting that item will take you into a sub-menu and you will be in ‘item select mode’ for that sub menu.

PUMA Control User’s Manual v1.2 | Page 32

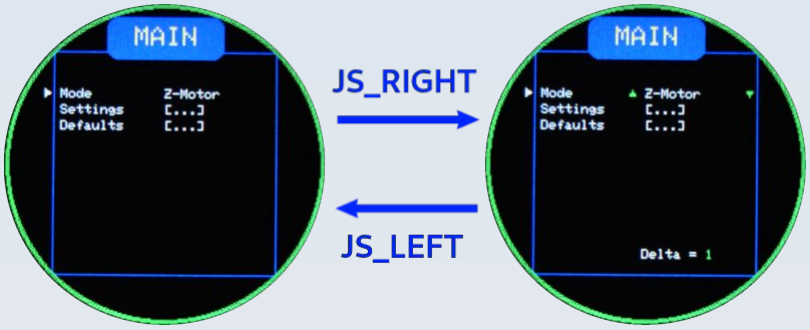
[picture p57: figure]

Figure 9. Menu modes and switching between them. Left: ‘Item select mode’ on the main menu. The arrowhead is pointing to the first item called ‘Mode’. You can move the arrowhead up and down to select a different item using the joystick up/down moves. If you want to edit the selected item then do a JS_RIGHT move on the joystick to enter ‘value editing mode’ on that item. Right: Value editing mode on the selected

item. This is signified by the appearance of green up/down arrowheads surrounding the item’s value, letting you know that you can alter that value my means of up/down movements of the joystick. The appearance of the ‘Delta’ value below also shows that you are in value editing mode but has no effect when editing non-numerical menu values. To get out of value editing mode back into item select mode just do a JS_LEFT move on the joystick (or press the ‘Reset’ button to go back a level or exit the menu altogether if you are in the main menu).

Value editing mode When you select a menu item (whose value is not ‘[...]’) with a JS_RIGHT action then you will see green up/down arrowheads surrounding the selected item’s value field and you will be in ‘value editing mode’ (figure 9). When in value editing mode, the value can be changed by moving the joystick up or down. Also, when you are in ‘value editing mode’ you will notice, near the bottom of the main square region of the display, the text ‘Delta =’

in white followed by some integer in green. This delta value is used when entering numbers – more on that shortly. You can leave value editing mode by one of two ways: 1. Perform a JS_LEFT move on the joystick to take you back to item select mode in the current menu.

2. Press the ‘Reset’ button to go back one menu level. If you are in a sub-menu this will take you to the main menu (and you will be in in item select mode) or if you are already in the main menu this will take you out of menu mode altogether and into the current control mode.
PUMA Control User’s Manual v1.2 | Page 33

Editing a menu item value: Strings and symbols

There are two types of value: a fixed list (of strings or symbols) and an integer number. For fixed lists of text strings or symbols moving the joystick up or down will take you through the options in succession. In some cases the list will cycle around, in others you can’t cycle. Once the option you want is displayed simply leave value editing mode and the displayed option will be used as the new value for that menu item.

Editing a menu item value: Numbers

For numbers you can also increment or decrement the value with the joystick (up or down) but you also have the additional control of how much to increment or decrement them by using the ‘Delta’ value mentioned above. The Delta value tells you how much you will change the current value by with each JS_UP or JS_DOWN key action. Delta can be any one of the following values:

1 10 100 1000 10000

You cycle through these options by clicking the ‘Select’ button while in value editing mode (the ‘Select’ button does nothing when you are in item select mode). Delta can be changed when a non-numerical fixed list value is selected for editing but Delta has no effect on non-numerical values. All numerical values will have limits you cannot go beyond. The limit will be dictated by the

nature of the value. For example, the ‘Backlight’ value can only be between 1 and 255 inclusive. You can only enter integer values with this method but there is a facility to enter a floating point number by considering the parts either side of the decimal point as separate integers and changing them separately. This is done when entering the calibration factor in the Defaults submenu (see below).

No negative numbers can be input (and none are required) in the current version of PUMA Control.

PUMA Control User’s Manual v1.2 | Page 34

Editing a menu item value: Colours

Many menu options allow you to select a colour for a particular feature. You may chose from any one of the following: Black, White, Custom, Red, Green, Blue, Yellow, Magenta, Cyan.
The choice is made by moving the joystick up or down to scroll through the list.
Colours are defined by a 16 bit unsigned integer using the Adafruit GFX library colour convention where the least significant 5 bits represent the blue component, the most significant 5 bits represent the red component and the intervening 6 bits are for the green component. A colour therefore has a numerical value between 0 (black) and 65535 (white) The fixed colour choices with their values are defined as follows (hexadecimal equivalent given in brackets): BLACK 0 (0x0000)

BLUE 31 (0x001F) RED 63488 (0xF800) GREEN 2016 (0x07E0) CYAN 2047 (0x07FF)

MAGENTA 63519 (0xF81F) YELLOW 65504 (0xFFE0) WHITE 65535 (0xFFFF) The value of the custom colour defaults to 39321 (0x9999) on startup and you can change it to any number (i.e. colour) you like via the ‘Defaults’ menu (see page 37). However, the

program will not allow the custom colour to be equal to one of the fixed colours so the lowest value you can chose is 1 (i.e. 1 more than pure black), the highest value you can chose is 65534 (i.e. 1 less than pure white) and if any other value you chose equals one of the fixed colour values shown above then your chosen value will automatically be incremented by 1.

Selecting multiple custom colours Each menu item that has a colour property has its own internal colour variable which is separate from the global ‘custom colour’ variable. When you select ‘Custom’ as the colour option for any menu item, the current value of the system’s global custom colour will be copied into the local colour property of that menu item. That menu item’s colour property

PUMA Control User’s Manual v1.2 | Page 35

will not automatically update to a new custom colour value when the system’s global custom colour value is changed by the user via the Defaults menu. If you want to update a menu item’s custom colour property to the latest one defined by the user then you must go to that menu item and change the colour property away from ‘Custom’ to some other colour and then back to ‘Custom’ (or cycle the colour outside the menu using the keypad interface for items that allow colours to be changed outside the menu – see for example page 65).
Although at first sight this may seem to be a limitation, it is in fact a deliberate design choice because this method enables multiple custom colours to be used simultaneously even though only one global custom colour value can be defined at any one time. As an example of how to do this I will discuss multi-custom-coloured apertures (see page 68 for detail about the Aperture menu and settings). Say you want 3 different custom colours for an aperture: clear aperture colour, background colour and central spot colour. First define the global custom colour value by setting the ‘Custom__col’ item in the

Defaults menu then go to the Aperture menu and select ‘Custom’ as the colour for your clear aperture colour. Now go back to Defaults and change the value of ‘Custom__col’ to your next custom colour value. Go to the Aperture menu and select ‘Custom’ for your background colour. This will only change the background colour value to the new custom colour, the clear aperture colour will retain the previous custom value. Finally go back to Defaults and change the ‘Custom__col’ value to your third custom choice then go back to

the Aperture menu and select ‘Custom’ as the colour for your central spot – this will only affect the central spot colour. So now you have loaded 3 different custom colours into your aperture settings even though you can only select one global ‘Custom__col’ value via the Defaults menu.

PUMA Control User’s Manual v1.2 | Page 36

### The Main menu

The main menu has three items: Mode, Settings, Defaults (figure 9).

Mode

Select this item to change the current control mode to one of the following: Z-motor, Pointer, Timer, Graticule, Plain, Aperture.
Details of what each of these modes do will be described elsewhere in this manual. For now note that each of these options has at least one item in a submenu that you can edit. This is the ‘Settings’ submenu and each control mode has its own ‘Settings’ submenu. You access the ‘Settings’ sub-menu for any control mode in one of two ways: Simply do a JS_MID while you are in the Mode value. This will take you directly to the settings submenu for that mode.

The ‘long way round’ is to first do a JS_LEFT to get back to the main menu selection, then do a JS_DOWN to select the ‘Settings’ item on the main menu then do a JS_RIGHT. Defaults sub menu The Defaults submenu has the following items (figure 10):

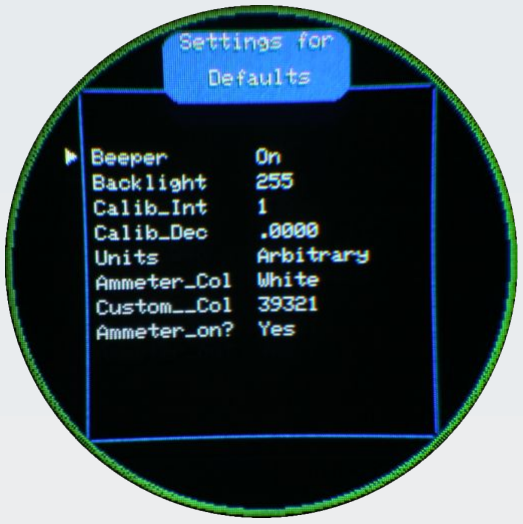
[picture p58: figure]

Figure 10. The Defaults sub-menu

PUMA Control User’s Manual v1.2 | Page 37

Beeper Value options: On, Off

This allows you to toggle the PCC in and out of mute mode. In mute no audio feedback will be provided with two override exceptions:
1. If the user has select an audio signal (including combined audio and visual signal) to mark the end of a count-down then that audio signal will be given even if the system is in mute mode.
2. If the lamp current exceed the upper limit then the audio alarm LAMPHOT will be sounded even if the system is in mute mode. Backlight Value options: Integer between 1 and 255 inclusive The brightness of the TFT screen backlight can be adjusted here. This is only relevant to the AR Projector for the HUD because the SLM TFT has no backlight. The dimmest value

is 1 and the brightest is 255. You cannot set a value of 0 (backlight off) partly because that would make the menu invisible but also because you can switch off the backlight in other ways while in certain control modes. Calib_Int Value options: Integer between 0 and 65535 inclusive The integer part of the calibration factor. See ‘Calibrating the HUD’ (page 40) for more details.

Calib_Dec Value options: Integer between 0 and 9999 inclusive The decimal fractional part of the calibration factor. Together with the Calib_Int this forms the floating point number used to calibrate measurements made with the HUD to real world units (the units specified in the next menu item). See ‘Calibrating the HUD’ (page 40) for more details.

Units Value options: Arbitrary, Millimetres, Nanometres, micrometres The real world units the HUD is calibrated to by means of the calibration factor. See ‘Calibrating the HUD’ (page 40) for more details. Ammeter_Col Value options: see page 35

The colour used for the lamp current meter reading. The default is white. If you select black then the ammeter reading will be invisible but this (and any other colour choice) will be over-ridden if the lamp current exceeds the upper limit. In that situation the lamp meter reading will appear in red (you don’t have the option to use red as a standard colour for this). Custom__Col Value options: An integer between 1 and 65534

PUMA Control User’s Manual v1.2 | Page 38

The value of the colour to use when a user selects ‘Custom’ as a colour option for any other colour setting in a menu. In order for the program not to get confused when selecting between colours in internal switch loops, the custom colour value must be different to any of the fixed colours. However, you do not need to consciously worry about this because if you select a value that is equal to one of the fixed colours (see page 35) the program will automatically increment your selected value by 1 (also the range limit 1 to 65534 prohibits you from selecting pure black or pure white).
When you change this value in the Defaults menu it only changes the value of the current global custom colour variable – it will NOT change the colour of any other menu items that you previously set to use ‘Custom’ as a colour choice. They will retain the custom colour that was in effect the last time you set them to use ‘Custom’. This is useful because it means you can set multiple menu items to use multiple different custom colours simultaneously even though you can only have one global ‘Custom__col’ value set here in the Defaults menu. To see an example of how to use multiple custom colours see page 35.

To to update a menu item that uses ‘Custom’ as it s colour you must ‘alter’ that menu option value again (even though that ‘alteration’ just means re-selecting ‘Custom’ again from the list of available colour options). While in value editing mode for that menu item you must first use the joystick to move the selection away from ‘Custom’ to one of the other fixed colours, then move back to ‘Custom’. This action will ‘re-load’ the current

custom colour setting into that option and it will be used for that item. For items that can have their colour changed interactively outside the menu system by using the keypad (for example, cycling the grid colour as described on page 65), the new Custom value will be loaded the next time the Custom option is selected via this method. Ammeter_on? Value options: Yes or No

Toggle between Yes and No using the joystick up/down. This determines whether the PCC monitors the current flowing to the microscopy lamp or not. It is on (‘Yes’) by default. Turning the ammeter off will mean that you will have no audiovisual warning if the microscope lamp is being over-driven (and so may burnout). The option to turn this off is provided because it is known that the ammeter system used by the PCC is unreliable for battery operation in that as time goes by and the batteries wear down the ammeter current reading rises until eventually a false over-current warning alarm is triggered. This will not happen when an external mains adapter power supply is used. Thus, in all cases where a mains adapter is used it is strongly advised to keep this setting as ‘Yes’. See the section on ‘Tripping the power regulator’ on page 16 for more details.

PUMA Control User’s Manual v1.2 | Page 39

## Calibrating the HUD

Measurements of lengths (including boundary lengths) of microscope specimens can be made using HUD with the Pointer and Graticule control mode features described in their respective chapters. This chapter discusses how to calibrate the HUD so those measurements can be expressed in real world units.

The native pixel resolution of the HUD The HUD is generated by the AR projector which projects and superimposes an image of an ST7789 TFT computer screen onto the back focal plane of the ocular lens of the microscope. Thus what you see in the HUD are the pixels of this TFT screen. The TFT screen is composed of 240 pixels horizontally and 240 pixels vertically as a

square array but the round field of view of the ocular lens means that you will not see all these pixels, the pixels in the corner regions being out of view. The HUD was designed to operate with oculars that have a 20 mm field of view – that means the image in the back focal plane of the ocular lens is 20 mm in actual diameter (physically there is a 20 mm diameter plane area in the barrel of the ocular that is visible to the observer). The AR projector was designed to project the image of the TFT screen to fill this area in X and Y

omitting the corners of the TFT screen in such as way that all the pixels just inside the green circle seen in the boot up and menu displays fits in the field of view of the ocular lens. So, depending on the actual arrangement of lenses in the AR projector (which can be adjusted by the user when setting up the scope) the visible HUD will consist in a circular area of pixels in a grid, 240 pixels in diameter. All lines drawn and all marks made by the

user on the HUD will be made on this pixel grid. Measurement units By default, when you first switch on the PCC, all measurement values are given in arbitrary units that represent HUD pixels – so if a line is stated to be 7.35 xm long it means

that the distance between the first and last pixel of that line is 7.35 HUD pixels. Measurement results and units appear in the bottom panel of the HUD in the ‘Pointer’ and ‘Graticule’ control modes (which see for further details). The units of measurement are selected via the ‘Defaults’ sub-menu (see page 37) and when displayed on the HUD the units are represented by two letters, the last one being ‘m’ (for metres). The full list of options and their HUD display abbreviations are:

PUMA Control User’s Manual v1.2 | Page 40

Arbitrary xm
Millimetres mm
Nanometres nm
micrometresmm

The default is ‘xm’ but the user can select any of the above options even if they don’t calibrate the scope as described below. Merely selecting a unit of measurement does not automatically make the scope calibrated to that measurement. It is the responsibility of the user to ensure an appropriate calibration factor is entered to make these measurement units mean what they say. The arbitrary (xm) option is provided so a user can use whatever calibration unit they like and are not restricted to the metric choices above but the user will have to make a note of what ‘xm’ means to them according to their own calibration (for example ‘xm’ could mean ‘hundredths of an inch’ if, for some reason, you wanted to calibrate the scope to that unit).

The need for calibration and factors affecting calibration As stated above, the initial default at boot up is that all measurement values are given in arbitrary units that represent HUD pixels. However, the size of these pixels have no standard or fixed relationship to the actual size of objects or the real distances between

points seen down the microscope because that will depend on the combination of the magnification of the object produced by the objective lens and the precise magnification of the TFT screen produced by the AR projector. So the relationship between HUD pixels and actual observed distances in some real world measurement unit needs to be worked out by a calibration procedure. It follows that every time you change the objective or change the magnification of the HUD

TFT projection image you will need to alter the calibration factor to one that is appropriate for that combination of lens arrangements. Changing the magnification of the TFT screen projection image will occur whenever you alter the distances between the AR projector lenses and its TFT screen by making adjustments to it and also by moving the ocular lens up or down and re-focussing the AR projector image on the new ocular position. Make sure you are aware of this – calibration factors are not just objective-specific.

How to calculate a calibration factor The calibration factor is the number of real world units per single HUD pixel (e.g. the number of micrometres per HUD pixel).

PUMA Control User’s Manual v1.2 | Page 41

To calculate a calibration factor, first set up your microscope and AR projector: select and install your objective, focus an image of a test specimen with it and ensure your AR projector is co-focussed and centred and ready to use. Do not change the arrangement of any lenses after doing this (with the sole exception of normal focussing of the stage). The calibration factor you calculate will only be valid for this particular arrangement of objective, ocular and AR projector.
Now place an object of know dimensions on the microscope stage. The most conventional way to do this is with a stage micrometer – i.e. a slide that has a 1 mm mark laser etched onto it with divisions of known length (as in figure 11).

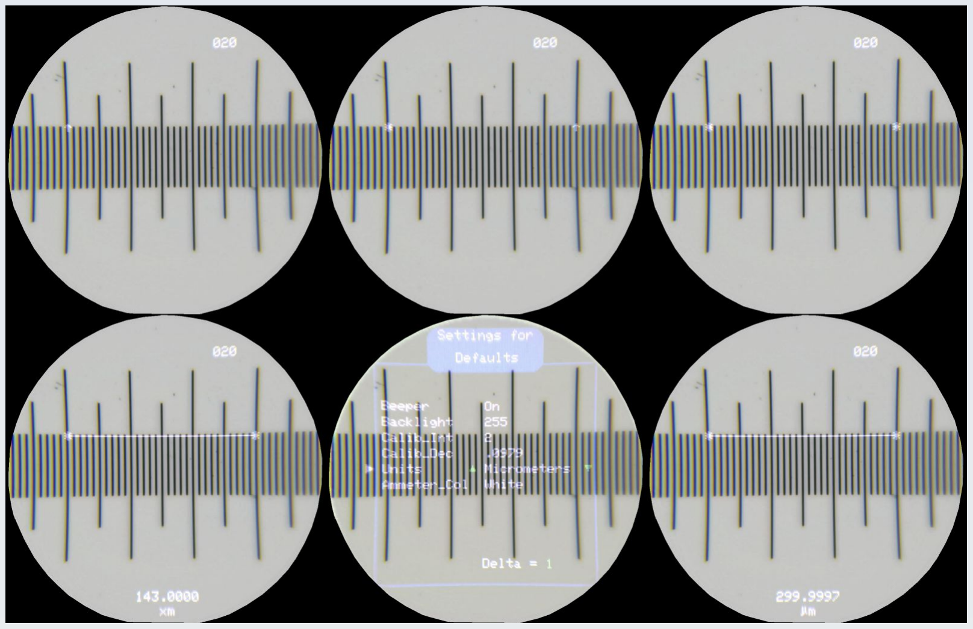
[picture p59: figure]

Figure 11. Calibrating the HUD with a stage micrometer which has 1 mm divided into 100 lines so each division line = 10 micrometres. This is a full field of view image through the ocular lens of a PUMA microscope set up with a x40 objective lens and the AR HUD. The procedure from top left through to bottom right is as described in the text. Top row: Left – HUD is in Pointer CM and the cursor (an up-arrow) is placed at one of the divisions of the stage micrometer. Middle – a mark was deposited at the last position of the cursor and it has now been moved to another division some distance away. Right – a mark is deposited there. Bottom row: Left – A line measurement is taken between the two marks and this shows the line to be 143 HUD pixels long. Middle – the calculated calibration factor (2.0979, see text) is entered into the Calib_Int and Calib_Dec items of the Defaults menu and the Units are edited to ‘micrometres’. Right – now when the user goes back to the Pointer CM they see that both the measurement value and units have been updated showing a value of 299.9997 micrometres (which is essentially correct because the line spans 30 divisions of the stage micrometer ruler, each division being 10 micrometres long). The number ‘020’ in the top right of the HUD is the lamp ammeter reading (20 mA).

PUMA Control User’s Manual v1.2 | Page 42

Select the Pointer control mode and draw a straight line on the HUD between two points on this known test object (see page 57 for information on how to do this). Note the length of this line in both real world units (from your knowledge of the test object, call this value X micrometres) and in HUD pixels obtained from the measurement function of the HUD (call this value Y pixels). As the default units used for measurements are HUD pixels Y is just the value of the measurement as shown on the HUD (unless the HUD was previously calibrated in which case you would need to change the calibration back to HUD pixels first by setting the calibration factor to 1.0 or reboot the PCC which will have the same effect). In the example shown in figure 11, Y = 143 HUD pixels.
In the example shown in figure 11, X is 300 micrometres because the line was draw to span 30 divisions of the stage micrometer and each division is 10 micrometres. Note that in figure 11 both the stage micrometer and the drawn line are completely horizontal. This is not necessary – what is necessary is that the drawn line be parallel to the stage micrometer. Both could be at 45 degrees for example – or any other angle so long as they are equal. The pixels in the HUD TFT are square and it is assumed that the microscope

optics have no significant astigmatism. This means that there is no need to do separate calibrations for horizontal and vertical directions and so the PUMA Control software has no facility to do separate axis calibrations. Having got the X and Y measurements you now use a calculator to calculate the calibration factor required to change HUD pixel units into real world units (we are using

micrometres in this example) like this: X= 300 micrometres Y= 143 HUD pixels Calibration_factor = X/Y = 300/143 = 2.0979 micrometres per HUD pixel

Inputting the calibration factor and units Now that you have a calibration factor, you need to input it into the PUMA Control software to allow all future measurements to be presented in these real world units. To do that go to the main menu, select ‘Defaults’ sub-menu and edit the ‘Calib_Int’ and Calib_Dec’ values to represent your calibration factor. This allows the input of a floating point number as two integers. For example if your calibration factor is 2.0979 you would

change Calib_Int to be ‘2’ and Calib_Dec to be ‘0979’. Next select the ‘Units’ menu item and change it to the units your calibration represents (micrometres in this example – see figure 11). Get out of the menus and back to Pointer control mode and the line you drew should now display with the measurement below updated to calibrated units (figure 11, bottom right).

PUMA Control User’s Manual v1.2 | Page 43

Any further length or distance measurements you make on any specimen (using this same objective and AR Projector setup) – whether by interactive cursor drawing or by a HUD graticule, ruler or scale bar – will have results calibrated to real world units.

PUMA Control User’s Manual v1.2 | Page 44

## Z-Motor

### General features

| automatic Z-sweep to start from a given position and also a ‘goto’ function that moves the Z-stage to a specified position. | Figure 12. The Z-Motor HUD. This is an example to

This allows the user to control the focussing Z-motor (figure 7, page Error: Reference source not found). This can be done by moving the joystick up and down with coarse and fine speed options but there are also some advanced functions such as setting up an

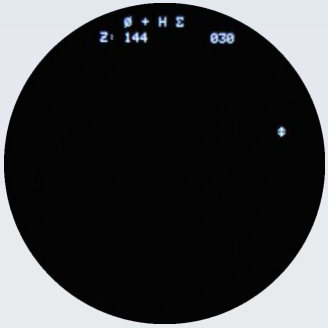
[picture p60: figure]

| | show where the information and icons for Z-Motor status are displayed on the HUD. The meaning of the following terms are all explained in the text. In this example the Z motor is homed (as indicated by the ‘H’) and is at position 144 steps above the homed (0) position. The motor coils are de-energised ( ), the user is in coarse (fast)
| | movement mode ( ) and is in sweep mode ( ). The user is in Z-Motor CM ( ) so key actions will have the effects described in this chapter. The number ‘030’ top right is the lamp ammeter display (it is drawing 30 mA) and is not related to Z-Motor functions.

When the user is in Z-Motor CM the up-down arrow icon ( ) will display in the right panel of the HUD (figure 12). This is important because information about the Z-motor and stage will usually be present all the time in the top panel of the HUD regardless of what CM is currently active, and users can easily toggle between the Z-Motor CM and other CMs so

seeing this indicator lets the user know that button the actions expected for the Z-Motor control mode will be done. Z-motor control (i.e. focussing) is such a enabled in all other CMs to allow toggling achieved by the SETRST combination key action (see page 25). | fundamental process that a special facility is to and from the Z-Motor CM. This toggle is | when they move the joystick or press any
PUMA Control User’s Manual v1.2 | Page 45

All Z-positions are measured in motor steps and cannot be negative. The homed position is 0. This is the lowest position the motor can be moved to. This is also the default Z-position value that is set when the PCC is switched on or rebooted but the Z position displayed has no meaning until the scope has been homed (the user will not be allowed to control the Z-motor until the scope has been homed). The current Z-position is constantly displayed in the top panel of the HUD. As the motor is moved to raise or lower the stage the number of individual motor steps are cumulated into this total Z-position value (steps expended in backlash correction when the motor changes direction are not included in this cumulative count). This position is an ‘open loop’ value i.e. there is no independent sensor that monitors the stage Z-position. For this reason the accuracy and repeatability of moving the stage to a given position as denoted by this Z-position value will depend partly on the mechanical accuracy of the stage construction, partly on the appropriateness of the backlash correction factor (to be discussed) and partly on the assumption that the motor gear or stage focus is not moved by hand or does not stall or slip at any time. The PUMA hardware only allows for a lower limit switch. There is no hardware control

over how high the stage can be lifted by the motor. To try and compensate for this a software limit has been hard-coded as 80000 steps (= ZPOS_MAX in the source code). This represents about 3.5 mm of Z motion which is almost the physical limit of how much the Z stage can move in its range. Any attempt to move the motor more than this number of steps will not be permitted. Of course, this being a software limit, it is easy to ‘fool’ the system into going above this (e.g. by manually adjusting the focus gears) but you risk

causing damage to the hardware if you do this. If the user attempts to move the motor beyond one of its permitted motion limits the motion will be aborted and the FORBIDDEN audio signal emitted.

PUMA Control User’s Manual v1.2 | Page 46

### Menu Settings

The Z-Motor CM sub-menu has the following options (see figure 13).

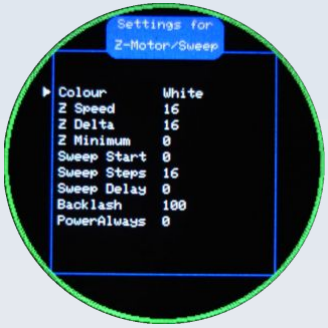
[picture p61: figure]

Figure 13. The options in the Z-Motor sub-menu. See text. Colour

The colour of the Z-Motor related information displayed in the HUD. Value options: see page 35 Default: White Z Speed

The delay (in milliseconds) between each change of the motor’s coil energisation state (i.e. between individual steps). The lower this value the faster the motor will turn but if you go too fast the motor is likely to stall. Early experiment with prototype showed that significant stalling occurred below 4 ms. If you experience motor stalling in your setup, increasing this value may help remedy the situation at the expense of slower motor revolution.

Value options: Integer in the inclusive range 4 - 65535 Default: 16

PUMA Control User’s Manual v1.2 | Page 47

Z Delta

The number of motor steps to move with each activation signal. This is the motion resolution. Using a value of 1 step (which translates to a Z movement of approximately 44 nanometres) gives the finest possible control with each up or down activation (an ‘activation’ is either a manual activation via the joystick or each automatic activation step that occurs as part of a sweep sequence). This resolution is probably too fine for most normal viewing and it will take a long time to move the focus even a very small distance so it is common to use a number greater than 1.
Value options: Integer in the inclusive range 1 - 4294967295 Default: 16 Z Minimum This is the lowest position that the Z-motor will be allowed to travel to. This is a software

lower limit for stage motion which allows the user to set a lower limit that is higher than the homed 0 position (because that level may be too low to prevent unwanted contact of objective with specimen, for example). Value options: Integer in the inclusive range 0 – 80000 Default: 0

Sweep Start An automated Z sweep may start from the current Z position of the stage or it may start from a specific Z position. This setting allows the user to set that specific Z position. Value options: Integer in the inclusive range ‘Z Minimum’ – 80000 Default: 0

Sweep Steps The number of steps an automated Z sweep goes through. Each of these steps will move the motor by ‘Z Delta’ motor steps (see above). Value options: Integer in the inclusive range 1 – (80000/’Z Delta’)

Default: 16 Sweep Delay The delay in ms between steps in an automated Z sweep. Value options: Integer in the inclusive range 0 – 4294967295

PUMA Control User’s Manual v1.2 | Page 48

Default: 0

Backlash

The number of motor steps (individual motor steps, not multiples of ‘Z delta’) that will be applied whenever the motor changes direction and will not be included in the cumulative total of motor steps that comprise the current Z position. This allows for compensation due to backlash slack in the gear system.
Value options: Integer in the inclusive range 0 – 1000
| Default: 640 PowerAlways A binary flag that dictates whether the motor coils remain energised after motion ceases (1) or not (0). If not then the motor coils are de-energised after each move in order to conserve energy and avoid the risk of coil overheating.
| Value options: Integer in the inclusive range 0 - 1 Default: 0 Homing the Z-motor
| Homing the stage, homing the scope and homing the Z-motor are all synonymous terms. The Z-motor will not move if the scope has not been homed. A user will not be allowed to toggle into Z-Motor CM from another CM using the shortcut toggle key combination (SETRST) if the scope is not homed. Upon boot up the scope will not be homed so the user must deliberately home the scope if they want to control focus or perform any functions with the Z motor. The scope doesn't home automatically upon boot up because
| if it homes while a specimen is on the stage this could damage the specimen as well as the objective / scope. This is because the homing process moves the stage as low as possible till the limit switch is triggered and for some objectives this could put the objective through the slide. The homed status of the scope is displayed in the top panel of the HUD. If a capital ‘H’ is present it means that the scope has been homed. If it is not present then the scope has
| not been homed.
Prior to homing, the user must ensure that the | limit switch | has been
appropriately fitted (as per hardware construction guides) otherwise damage to the microscope may result.
The Z-homing process can be initiated in three ways:
PUMA Control User’s Manual v1.2 | Page 49

1. Deliberately from the boot up screen by pressing the ‘Set’ button
2. Deliberately when in Z-motor CM by a combination press of SETDOWN (see page 25). This only works if the user is NOT in sweep mode – see below for details.
3. Whenever the Z-Motor CM is entered (from the menu) and the scope is not homed, the user is presented with the notice 'Z MOTOR IS NOT HOMED'. Press ‘Reset’ to exit this warning and go straight to the motor control mode (but you won't be able to use the motor until you go through with homing). Press any other button (i.e. except ‘Reset’) to clear this message and begin the homing sequence.
When homing is initiated: • You will be advised, via the GUI, to remove the specimen from the stage and perform a JS_MID action (see page 25) to begin homing. The GUI notice actually says ‘PRESS CENTRAL BUTTON’ rather than using the ‘JS_MID’ abbreviation but it means the same thing.
- You can abort the homing process at this point by pressing something other than JS_MID but you wont be able to operate the motor until you have homed the stage. If you have previously homed the stage and are initiating another homing cycle then you will be able to use the motor on the basis of the previous homing. • Once you perform the JS_MID action homing will commence and cannot be interrupted by any key action (you would have to manually intervene by, for

example, switching off the PCC in order to stop this). • After homing is successfully completed the current Z position displays 0 and the ‘H’ symbol will be displayed in the top panel of the HUD. Once the motor is homed, it cannot be ‘un-homed’ other than by performing a re-boot of the PCC. However you can re-home the scope at any time. For example if you disturb the

Z position by manually moving the focus you can do another homing procedure to reset the current Z position counter to 0. Sweep mode and ‘Goto’ There are two Z-Motor modes: standard and sweep. You toggle between these two

modes by a right move on the joystick (either alone or in combination with the ‘Set’ button). See page 25 for the meaning of the following key action abbreviations. When in sweep mode SETDOWN triggers a downwards sweep from the current Z position. When in standard mode the SETDOWN action initiates a homing request.

PUMA Control User’s Manual v1.2 | Page 50

When in sweep mode SETUP triggers an upwards sweep from the current Z position. When in standard mode SETUP does nothing.
When toggling between the modes JS_RIGHT just toggles between the modes. However a SETRIGHT combo action does this:
- When in sweep mode it simply toggles to standard mode - the same as if a JS_RIGHT action were made.
- When in standard mode it toggles into sweep mode and causes the scope to first 'goto' the start position for a sweep as set in the menu settings but it does not initiate the sweep itself. This functionality can also be used as a plain 'goto a set position' facility because you can activate it from standard mode then go straight back into standard mode if you wish. Summary of Z-Motor HUD icons

All these appear in the top HUD panel except the which appears on the right panel (see figure 12). You are in Z-Motor control mode H The Z-motor has been homed The motor coils are not energised

The motor coils are energised in a pattern that will move the stage upwards when the motor is stepped. The motor may or may not currently be stepping (moving). If the motor is not moving and this icon is displayed it means that the motor was moving in that direction previously and has now stopped but the coils remain energised. The motor coils are energised in a pattern that will move the stage downwards

when the motor is stepped. The motor may or may not currently be stepping (moving). If the motor is not moving and this icon is displayed it means that the motor was moving in that direction previously and has now stopped but the coils remain energised. The system is in coarse focus mode. This means the speed is at the maximum possible setting (a delay of only 4 ms between steps) regardless of the user’s chosen Z

speed in the menu. The system is in sweep mode.

PUMA Control User’s Manual v1.2 | Page 51

### Keypad actions for the Z-Motor CM

See page 25 for the meaning of the key action abbreviations.
JS_UP | : Move stage Z-delta motor steps upwards
JS_DOWN : Move stage Z-delta motor steps downwards JS_LEFT : Toggle between coarse and fine focussing (with icon)
JS_RIGHT : Toggle between standard and sweep mode (with icon)
JS_MID : Toggle the backlight on and off if a homing request has not been initiated, otherwise this begins the homing procedure. SET_BTN : SET : De-energise the motor coils (with icon). The motor will re-energise (and the de-energised icon cleared) whenever the motor is reactivated.

SETRST : Select the previous non-Menu CM as current control mode. SETDOWN : Initiate a request to home the Z motor if in standard mode or start a downward sweep if in sweep mode. SETUP : Do nothing if in standard mode or start an upward sweep if in sweep mode.

SETMID : No action. SETLEFT : Click the Set button in combination with JS_LEFT SETRIGHT : Toggle between standard and sweep mode (with icon) but if toggling into sweep mode perform a ‘goto’ action by moving the Z motor to the ‘Sweep Start’ Z coordinate specified in the settings. Do not initiate the

sweep, just go to that position and wait for the user to take the next step. RST_BTN : Enter the main Menu (or clear the 'Z MOTOR IS NOT HOMED' warning if this is displayed)

PUMA Control User’s Manual v1.2 | Page 52

## Pointer

### General features

This allows the user move a cursor around the HUD and, optionally, to deposit marks on the display. The cursor is moved via the up, down, left, right and diagonal motions of the joystick and a mark is deposited at the current location of the cursor by means of a JS_MID key action (see page 25 for an explanation of how to perform this and other key actions referred to in the chapter).
These marks can be used to highlight features, count objects and measure distances and angles. Although this is called ‘Pointer’ CM, the cursor can be any one of a number of shapes, not just arrows.

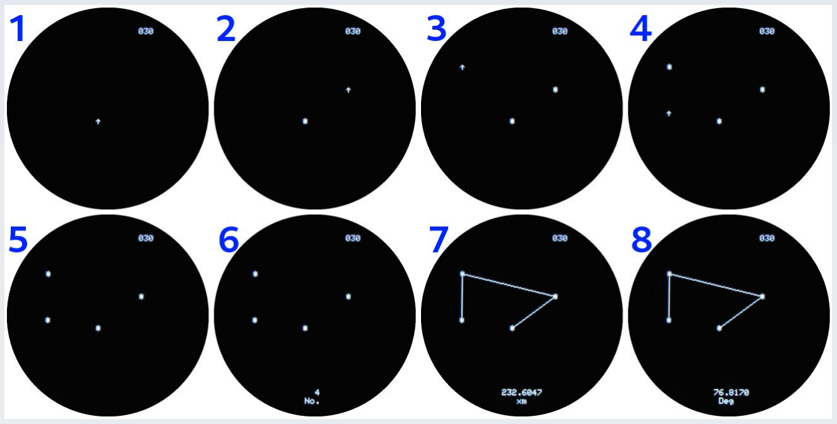
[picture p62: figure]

Figure 14. Pointer marking and measurements. This shows a simple sequence of pointer moves (using the cursor) to 4 positions with a mark ( ) laid down at each position by the user (images in sequence from 1 to 5). Images 6 to 8 show the three types of measurements that can be made with these marks as detailed

in the text. The number ‘030’ at the top right of each image is the lamp ammeter reading (30 mA) and is not related to the Pointer functions. This CM provides a ‘pointer only’ mode (figure 14, images 1 to 5) and 3 additional measurement modes for counting, lengths and angles (figure 14, images 6 to 8). The default mode is pointer only. Other modes are selected (cycled) using the SET button as follows:

PUMA Control User’s Manual v1.2 | Page 53

1. Pointer: Move a cursor character about with the joystick and deposit marks but no results are displayed i.e. the screen is blank except for the cursor and any deposited marks (and any HUD information from the Z-Motor, Timer and lamp ammeter).
2. Counter: As for the above but the measurement results HUD panel is displayed (the lower panel) showing number of marks deposited (figure 14, image 6).
3. Length: A (poly)line is drawn between all marks laid down by the user and the length of the (poly)line line is displayed in the the measurement HUD panel (figure 14, image 7). This will be in units calibrated by the calibration factor set in the menu (see page 40). You need at least 2 marker points for a line length to be calculable. The FORBIDDEN buzzer signal will sound if you try to read a length from fewer than 2 marks. 4. Angle: A (poly)line is drawn between all marks laid down by the user and the angle between the last two lines drawn is displayed in the the measurement HUD panel

(figure 14, image 8). This is in degrees and is the smaller of the two possible angles so will be between 0 and 180 degrees. You need at least 3 marker points for an angle to be calculable. The FORBIDDEN buzzer signal will sound if you try to read an angle from fewer than 3 marks. The joystick can't be used for both pointer movement and Z-motor focus control

simultaneously so a quick toggle between the pointer control mode and the Z-motor control mode is provided by the SETRST combination key action. The coordinates of all marks laid down by the user are stored in global memory arrays so will be preserved when the user switches over to the menu or any other CM (including the Z-motor CM) so will be preserved when they return to the Pointer CM. Because this global storage uses the limited PSRAM of the Arduino Nano the maximum number of points you

can mark is quite limited and, in the current version of PUMA Control, this upper limit is set at 127 marker points. The marker point character is selected by the user via the Pointer settings menu (see below). Different characters are optimal for different uses. For example, if you want to trace the outline of a complex shape this will require many segments to the poly-line and possible many marker points laid down close to each other. In this scenario it is often best

to use the single pixel marker character because these will effectively only show the poly-line and will not complicate the line with larger marker characters closely crowded over each other. You can change the marker character at any time without having to re-draw the poly-line manually – whenever you go to the menu to select a new colour or character and then return to Pointer CM, all previously laid down marker points will be drawn with the newly chosen settings.

PUMA Control User’s Manual v1.2 | Page 54

To clear all marks and reset the count to perform a SETMID combination key action. You may want to do this prior to measuring a new line or a new angle. You will be prompted prior to deleting all marks because this cannot be undone. Performing the simple JS_MID key action after the prompt will delete the data. Pressing any other button will abort the delete request and return the user to where they were before.
The speed of motion of the cursor can be adjusted by the SETUP or SETDOWN combination key actions. Slowing down the motion of the cursor makes it easier to place it at a precise location.
You can undo and redo marks – in the reverse order to which they were laid down – using the SETLEFT (for undo) or SETRIGHT (for redo) combination key actions. No matter how many marker points you ‘undo’, you can ‘redo’ all points that you have ‘undone’ all the way to the most recently added marker point. For example if you lay down 73 points and you undo all of them, you can redo all 73 points provided you don’t add any new marker points. As soon as you add a new marker point then that becomes the ‘last point added’

and you can’t ‘redo’ any more points beyond that. So in this example if you ‘redo’ points up to the 50th point and, at that stage, you add a new marker point then you can’t continue to redo any of the previous 73 points beyond the 51st point you have just added. Menu Settings The Pointer CM sub-menu has the following options (figure 15).

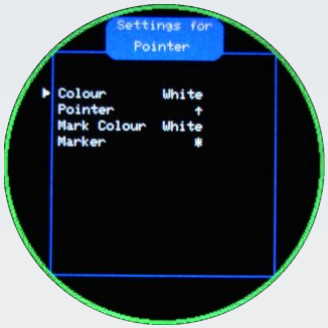
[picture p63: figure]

Figure 15 Pointer sub-menu.

PUMA Control User’s Manual v1.2 | Page 55

Colour

The colour of the cursor (not the markers or other text of the HUD). Value options: see page 35

Default: White

Pointer

The cursor character (as distinct from the marker point character) Value options: , , , , , , , , , , , Default: Marker Colour The colour of all markers laid down and also the measurement text.

Value options: see page 35 Default: White Marker The character to use when laying down marker points.

Value options: , , , , , Default:

PUMA Control User’s Manual v1.2 | Page 56

### Measure the length of a line or boundary

All necessary information to do this has been presented above but it may help to go over a complete measurement procedure from start to finish (see figure 16).

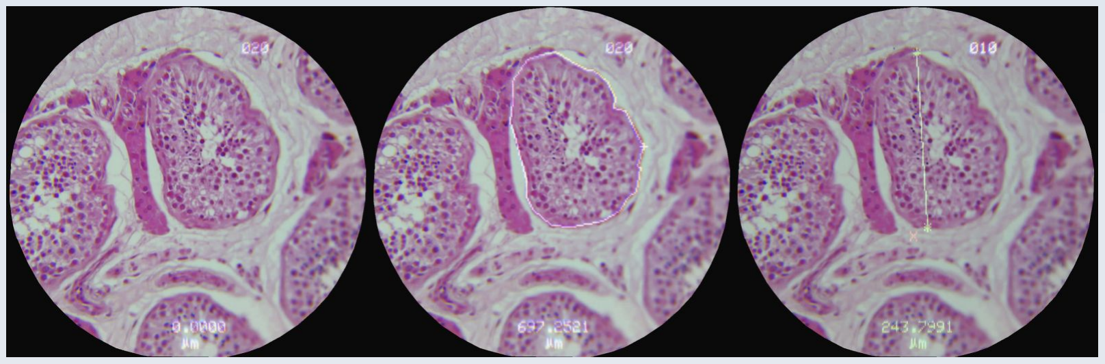
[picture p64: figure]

Figure 16. Examples of using Pointer CM to measure a boundary and and line (a diameter) of a seminiferous tubule in an H&E-stained histological section of testis. Left: No marks yet laid down, the lamp ammeter reading shows top right and the measurement below (currently 0) with the symbol for micrometres as units (this HUD was calibrated to micrometres). Middle: The boundary of the selected tubule has been traced by placing multiple marks along its border. In this case the single pixel marker has been selected so all you see is the boundary. All text and graphics are in the default white colour. The boundary measures 697.2521 microns. Right: The previous marker points were deleted and just two marker points laid down at opposite ends of the tubule to measure this diameter line. Note that the colours have been changed via the menu. Green for marks and other text and graphics, red for the cursor. The cursor has been changed to an and the marker character has also been changed to an . The line measures 243.7991 micrometres. 1. Via the menu select your choice of colours and cursor / marker characters

2. When in pointer control mode move the cursor, with the joystick, to one end of the line and perform a JS_MID key action to lay down a marker character. 3. Mover the cursor to the other end of the line and perform a JS_MID key action to lay down another marker character. 4. Press the SET button (on its own) repeatedly until the length measurement result appears on the bottom HUD panel.

That’s it. The result will be in whatever units you have previously calibrated the system in (see page 40) or it will be in HUD pixels if the system has not been calibrated.

PUMA Control User’s Manual v1.2 | Page 57

For boundary measurements the procedure is similar. However in this case you will be creating a poly-line by continuing to lay down marker points at intervals along the boundary of the object to be measured. If you are measuring a closed boundary be sure to lay down a final marker point at the same position as the very first marker point (so the first and last marker point are superimposed on each other).
For tracing and measuring complex lines and boundary shapes that may require many marker points in close proximity to each other (so you can accurately follow tight curves and turns) it will usually be best to select the single pixel marker character ( ) because this avoids a messy and overly complex display of overlapping marker characters and will effectively just show the poly-line on its own. This can be seen in figure 16. Keypad actions for the Pointer CM

See page 25 for the meaning of the key action abbreviations. In Pointer CM there will be no buzzer ACKNOWLEDGED signal when moving the cursor around. Also, the amount of auto-repeat delay for holding the joystick in one position is set by the user by altering the combined movement in the } diagonal directions. pointer speed as described below. JS_UP : Move cursor up one pixel In Pointer CM you may also move the joystick in any of the JS_DOWN : Move cursor down one pixel

four 45 degree diagonal JS_LEFT : Move cursor left one pixel directions to produce a JS_RIGHT : Move cursor right one pixel JS_MID : Place a mark at the current cursor position and update any count or measurement. If you have initiated a ‘delete all marks’ action and are being prompted if you really want to delete all, then perform a JS_MID key action to confirm delete.

SET_BTN : SET : Cycle between pointer, counter, length and angle modes SETRST : Select the Z-motor CM as current control mode. SETDOWN : Decrease the cursor motion speed

SETUP : Increase the cursor motion speed SETMID : Reset the marker count to zero (delete all marks). SETLEFT : Undo the previous marker SETRIGHT : Redo (replace the last marker that was 'undone') RST_BTN : Enter the main Menu

PUMA Control User’s Manual v1.2 | Page 58

## Timer
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

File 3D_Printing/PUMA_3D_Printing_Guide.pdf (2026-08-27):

# PUMA 3D Printing Guide

Document created: 26.02.2021, Last edited: 27.08.2026

PUMA: The Open Source (GPL v3.0) 3D printed microscope system designed for direct eye observations and ultra-portability with advanced options for digital imaging, measurements and computer control.

## Contents

PUMA 3D Printing Guide v1.3 | Page 1 of 362

PUMA 3D Printing Guide v1.3 | Page 2 of 362

PUMA 3D Printing Guide v1.3 | Page 3 of 362

PUMA 3D Printing Guide v1.3 | Page 4 of 362

PUMA 3D Printing Guide v1.3 | Page 5 of 362

CN_SD_Letters_PUMA | 163
CN_SD_T_nut_positioner | 164
CN_SD_XMotor_cover_L | 165
CN_SD_Xmotor_cover_R | 165
Dominus Illumination System | 166
Location of the models | 166
Resources | 169
DI_Cnd_Adj_thumbwheel | 173
DI_Cnd_Crosshair_Cap_c_adhesin | 174
DI_Cnd_Flange_Spacer_0p48 | 175
DI_Cnd_gripper | 176
DI_Cnd_Mirror_holder_socket | 177
DI_Cnd_protector_cap | 178
DI_Cnd_to_UC | 179
DI_Cnd_to_UC_long | 180
DI_Collector_mirror_block | 181
DI_Mirror_block_spacer | 182
DI_Condenser_23_30 | 183
DI_Condenser_base | 184
DI_Daylight_Kohler_adaptor | 185 DI_Epi_attachment | 186 DI_Epi_black_body | 187 DI_Epi_cap | 188 DI_Epi_Cnd_Aperture_04 | 189
DI_Epi_Cnd_Aperture_10 | 190 DI_Epi_Cnd_Aperture_13 | 191 DI_Epi_condenser | 192 DI_Epi_pol | 193 DI_Ferrule_46_c_adhesin | 194
DI_Field_Stop_Rectangle | 195
DI_Field_Stop_Round | 196
DI_HNA_Diffuser | 197
DI_HNA_Flange_Spacer_0p48 | 198
DI_HNA_Illuminator | 199
DI_IAD_AP_25mm_oil | 200
PUMA 3D Printing Guide v1.3 | Page 6 of 362

DI_IAD_AP_DF_Stop_10 | 201
DI_IAD_AP_DF_Stop_11 | 202
DI_IAD_AP_DF_Stop_12 | 203
DI_IAD_AP_DF_Stop_2p5 | 204
DI_IAD_AP_DF_Stop_oil_20 | 205
DI_IAD_AP_Phase180_oil | 206
DI_IAD_AP_Phase180 | 207
DI_IAD_Filter_Tray_oil | 208
DI_IAD_Filter_Tray | 209
DI_IAD_SLM_Cover | 210
DI_IAD_SLM_Filter | 211
DI_IAD_Tray | 212
DI_IFD_Adapter | 213
DI_IFD_Extension | 214
DI_IFD_Filter_crosshairs | 215
DI_IFD_Threadjoiner | 216
DI_IFD_Threadlock | 217
DI_IFD_Tray | 218
DI_LC_Adjust_collar | 219
DI_LC_Cap | 220
DI_LC_Collar_2 | 221
DI_LC_Collar_7 | 222
DI_LC_Receptacle | 223
DI_LC_Spacer | 224
DI_LED_Cover | 225
DI_LED_Holder | 226
DI_LED_Washer | 227
DI_LPC_Lensholder | 228
DI_LPC_Lens_retainer | 229
DI_LPC_Lensless_23 | 230
DI_LPC_Single_23 | 231
DI_M3_Adjustment_ring | 232
DI_M3_Adjustment_ring_Kohler | 233
DI_M3_Thumbscrew_short_hex | 234
DI_M3_Thumbscrew_tall | 235
PUMA 3D Printing Guide v1.3 | Page 7 of 362

DI_Mirror_holder_plain | 236
DI_Mirror_suspend_plain | 237
DI_Mirror_to_baseplate | 238
DI_PWG_CM_Aperture_12 | 239
DI_PWG_Front_stop_12 | 240
DI_PWG_Front_stop_16 | 241
DI_PWG_Pinhole_mount | 242
DI_PWG_Pinhole_mount_washer | 243
DI_PWG_Pinhole_mount_well | 244
DI_PWG_Pinhole_plain | 245
DI_PWG_Pinhole_presser | 246
DI_PWG_RMS_to_LC | 247
DI_PWG_Tripod | 248
DI_PWG_WindowCap | 249
DI_Pol_Adjustment_ring | 250
DI_Pol_middle | 251
DI_Pol_Receptacle | 252
DI_Pol_to_baseplate | 253
DI_Pol_top_bottom | 254
DI_Proximal_collector_attachment | 255
DI_Tool_23 | 256
DI_Tool_44 | 257
DI_UC_Retention_Cap | 258
DI_UC_Spacer | 259
DI_Uber_pol | 260
DI_Youngs_frame | 261
DI_Youngs_slit | 262
Filterblock | 263
Resources | 263
FB_Filter_block_simple | 264
FB_Filter_collar_compression_tool | 265
FB_Filter_collar | 266
FB_Filter_F17_slider | 267
FB_Filter_F_slider | 268
FB_Filter_slider | 269
PUMA 3D Printing Guide v1.3 | Page 8 of 362

FB_Filter_Slot_bottom | 270
FB_Filter_slot_stopper | 271
FB_Filter_slot_top | 272
FB_Infinity_adapter | 273
FB_Side_port_separate | 274
FB_Side_port_separate_EpiStop | 275
FB_Splitter_case | 276
FB_Stopper | 277
FB_Top_connector | 278
Focus Gears | 279
Resources | 279
FG_Fine_gear | 280
FG_Focus_spacer | 281
FG_Intermedius | 282
FG_Pulley_coarse | 283
FG_Pulley | 284
FG_Eccentric_Tensioner_Top | 285
FG_Eccentric_Tensioner_Bottom | 286
FG_Eccentric_Tensioner_Pulley_c_adhesin | 287
Legs | 288
Resources | 288
LG_Back_leg_angled | 289
LG_Feet_linker | 290
LG_Front_legs | 291
LG_Hind_extension | 292
LG_Short_leg | 293
Monocular Head | 294
Resources | 294
MN_EM_Block | 295
MN_EM_Block_cover | 296
MN_Monocular_tube_c_adhesin | 297
MN_Monocular_tube_CM_c_adhesin | 298
MN_Ocular_cap_170 | 299
MN_Ocular_cap | 300
MN_Ocular_extension_c_adhesin | 301
PUMA 3D Printing Guide v1.3 | Page 9 of 362

MN_Ocular_extension_CM_c_adhesin | 302
MN_Ocular_Extn_CM_170_c_adhesin | 303
MN_Ocular_lock_nut | 304
MN_Ocular_protective_cap | 305
MN_Ocular_tube_protective_cap | 306
MN_Projector_cone | 307
MN_Aperture_20mm | 308
MN_Aperture_46mm | 309
PUMA Control Console | 310
Resources | 310
PC_Battery_cover | 311
PC_Expansion_port_cover | 312
PC_Front_panel | 313
PC_Joystick_PCB_clasp | 314
PC_Lamp_insulator | 315
PC_Left_panel_Base_Skeleton | 316
PC_Top_back_panel | 317
PC_Ardu_cover | 319
PC_Current_knob | 320
PC_Monitor_case | 321
PC_Monitor_connector | 322
PC_Monitor_lens_retainer | 323
PC_Monitor_light_shield | 324
PUMA Lite | 325
Resources | 325
PL_Battery_cover | 326
PL_Knob | 327
PL_Lamp_insulator | 327
PL_Left_Base_Back | 328
PL_Top_Front_Right | 329
Quick Release Objective Holder | 331
Resources | 331
QR_Base_thread | 332
QR_C-RMS_Thread | 333
QR_Male_C_extn_1mm | 334
PUMA 3D Printing Guide v1.3 | Page 10 of 362

QR_Male_C_extn_4mm | 335
QR_Trainer | 336
QR_Trainer_Male | 337
Stabiliser | 338
Resources | 338
SB_S1_Axial | 339
SB_S1_Insert_c_adhesin | 340
SB_S1_Lateral_strut_Left | 341
SB_S1_Lateral_strut_Right | 343
SB_S1_Peg | 344
Stage | 345
Resources | 345
ST_Articulation | 346
ST_BasePlate | 347
ST_FocusPlate | 348
Trinocular Camera Port | 349
Resources | 349
TN_Trinoc_CP_tube | 350
TN_Trinoc_CP_CM | 351
TN_Ocular_spacer_ring_1p44 | 352
XY Stabiliser | 353
Resources | 353
XY_Stabiliser | 353
Z-Motor | 354
Resources | 354
ZM_Motor_attachment | 355
ZM_Motor_gear | 356
ZM_Z_Limit_Sw_Mount | 357
ZM_Z_Probe | 358
ZM_Z_Yoke | 359
PUMA 3D Printing Guide v1.3 | Page 11 of 362

## Legal Information

## License

Copyright (C) 2021-2026 Dr Paul J. Tadrous
Permission is granted to copy, distribute and/or modify this document under the terms of the GNU Free Documentation License, Version 1.3 or any later version published by the Free Software Foundation; with no Invariant Sections, no Front-Cover Texts, and no Back-Cover Texts. A copy of the license can be found at https://www.gnu.org/licenses/fdl-1.3.html Limitations of Use The PUMA microscope and its associated systems do not have any certifications or

regulatory approvals in any country for use in clinical diagnostics or treatment (human or veterinary). The PUMA microscope and its associated systems are released to be used for research and educational purposes only.

Disclaimer All PUMA project information, including without limitation any CAD file (or 3-dimensional (3D) model or mesh file in any other format) and all documentation, advice and instruction (whether provided in video form, audible form, written form or otherwise) is provided ‘as is’ in good faith and is intended to be helpful but comes with no warranty whatsoever. Anyone attempting to build or use a PUMA microscope or other PUMA-related material,

accessory, module or derivative is hereby advised that there will be risk involved in 3D printing, post-print processing, assembly and usage of the resulting structures. This risk includes, without limitation, the risk of personal damage and loss of resources. Dr Paul J. Tadrous, TadPath and OptArc cannot accept any liability for any such loss or damages that may occur. All those who attempt to build or use any aspect of the PUMA project or derivatives thereof do so at their own risk.

PUMA 3D Printing Guide v1.3 | Page 12 of 362

## Health and Safety Advice

## Burns and Fire

There is a risk of fire and of burns when working with 3D printers, soldering irons and molten solder. Wear appropriate personal protective equipment such as gloves and eye and face protection. Ensure all electrical components are of the appropriate voltage and current tolerances. Do not leave electrical components powered for longer than they are required for use. Do not leave 3D printers unattended when they are powered up.
Toxic Fumes Some filaments used in 3D printing can release toxic fumes when heated (such as during the 3D printing process). Working with solder can also release toxic fumes (especially if leaded solder is used). Ensure adequate ventilation at all times during 3D printing and soldering.

Lacerations Cleaning and assembling 3D prints and other components of PUMA systems sometimes involves the use of sharp instruments – take appropriate precautions when handling sharp blades. Working with optics – especially thin plates of glass such as beamsplitter mirrors, microscope slides and coverslips and display screen panels can result in flying shards and sharp edges. Wear appropriate personal protective equipment such as gloves and face and eye protection.

Injury to Eyesight Physical injuries to the eyes may occur from shards and specs of glass and airborne particles of molten or hot solder. Bright lights are used to illuminate the PUMA microscope. These should be used with caution. Do not stare directly into the illumination LED bulb (with or without its collector lenses in place), and only use a brightness setting that is appropriate for comfortable viewing when using the complete

microscope. If using a mirror to provide illumination always use a reflection from a diffuse scene such as an open blue or cloudy sky. NEVER allow specular reflections of the sun to enter the field of view of the mirror or permanent eyesight loss may result. If using a bulb that emits UV light, always ensure an appropriate and effective UV blocking filter is used to shield your eyes from the UV light. If a laser is used for illumination then you should never look at the image through the lenses of the scope (you should use a camera for making observations).

Protecting the Vulnerable The PUMA microscope and its accessories are not toys. Do not allow children, vulnerable adults or pets to come into contact with any PUMA product without appropriate supervision and safeguards.

PUMA 3D Printing Guide v1.3 | Page 13 of 362

## Introduction

PUMA is a 3D printed high quality microscope system. The name PUMA stands for Portable, Upgradeable, Modular and Affordable – key features of this system.
This document provides practical advice for those who want to print their own parts for the building of PUMA-related modules and microscopes.
It also serves as a visual ‘index of parts’ for all the 3D printed parts in the PUMA project and shows which FreeCAD file contains which parts. Within the FreeCAD file those models have the same name as the printable model file but without the printable file extension (like ‘.stl’ or ‘.3mf’) and also without the two letter prefix before the first underscore. For example, the printable file ‘AR_Cc_locknut.stl’ is a mesh generated from the model called ‘Cc_locknut’ in the FreeCAD file called ‘AR_Projector.FCStd’. The information in this file only relates to 3D printed parts. To build a PUMA microscope additional components will be needed such as nuts and bolts and optics elements. None of these additional components are addressed here. See the assembly / usage tutorials, videos and other ‘how to build’ documentation for that information. At the beginning of each section some general printing advice (like slicer settings

profile) is given if the models for that section are to be printed with a profile other than the default (to be discussed later). Futher advice is given for each model separately. For most models this advice consists solely in an illustration showing the preferred orientation of the model on the printer build plate. In some cases additional advice and illustrations are given, particularly where they relate to support structures. This document makes no attempt at explaining what each part does or how to use or assemble them. For that kind of information you would need to see the assembly /

usage tutorials and other documentation. The Cura screenshot illustrations in this document show the models at various zooms and with some angular perspective variations from model to model in order to emphasise different aspects. However the grid and ‘Ender’ logo shown on the build plate should make it clear how the model is to be orientated and indicate the scale. Each chapter begins with a table of resources showing the print time and length of 1.75 mm diameter PLA filament used to print each model file as estimated by Cura v.4.8.0

using the recommended print settings described in that chapter for each model.

PUMA 3D Printing Guide v1.3 | Page 14 of 362

## Cover Illustration

## Centre

A PUMA microscope in the following configuration: Full Kohler illuminator, motorised Z-stage, mechanical XY Vernier caliper slide holder, advanced filter block, augmented reality projector, binocular head, PUMA control console. It is fitted with a Zeiss Plan 2.5x objective and two high eye point wide field 10x oculars of 20 mm field of view. Many alternative configurations are possible due to PUMA’s modular design.
From Top Going Clockwise These microscope images (all taken with a PUMA microscope in various configurations) are highly cropped and compressed and do not show the full field of view. See the gallery of images on the PUMA websites for full quality and full field images. Magnifications given below are of the objective only: Bright field Kohler illumination: H&E chronic inflammation, x100 oil immersion.

Fluorescence microscopy: Fluorescein stained Soncus bud showing pollen grains and other cellular structures x40. Fluorescence microscopy: Fluorescein stained Ilex (holly) leaf showing chloroplasts, vascular structures and other cellular structures x40. Crossed polarisation microscopy: Amyloid stained with Congo red x40. Dark field / Dark ground microscopy: Unstained section of colonic tissue x10.

Schlieren phase contrast using a spatial light modulator in the illuminated aperture plane of the condenser: Unstained section of colonic mucosa, x100 oil immersion. Crossed polarisation microscopy: Striated muscle of tongue stained with H&E x40. AR HUD Overlay. The figure shows a cropped area from a small part of the field of a x10 view of an H&E section (of testis) with the augmented reality (AR) projector projecting a heads up display (HUD) of a

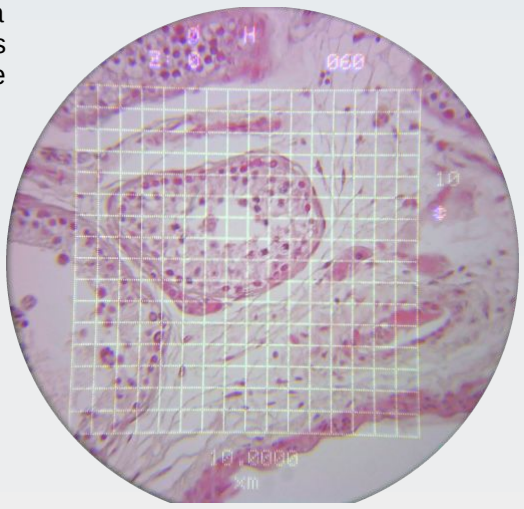
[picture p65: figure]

grid and some microscope status information onto the live optical image. The full field image is shown here:

PUMA 3D Printing Guide v1.3 | Page 15 of 362

## Generating Files for 3D Printing from the FreeCAD Source Files

In previous editions of this document I used mainly STL mesh files for 3D printing. I have since moved away from favouring STL in favour of 3mf files as I found that STL files could sometimes be excessively large (in terms of megabytes) and might not load properly (or take excessively long to load) in the slicer program that I use (Cura) as well as other slicers. Furthermore, STL file generation with FreeCAD requires an intermediate processing step on the models (to turn them into meshes) but FreeCAD models can be saved directly as 3mf files without any processing. This latter distinction became especially importance since some bugs have crept into later models of FreeCAD which do not allow the reading of older FreeCAD files properly once they are imported into the new FreeCAD version and ‘recalculated’ for processing. This means that, until such bugs are fixed, some of the older models cannot be edited in FreeCAD (such as to make them into meshes) but they can be read and directly saved as 3mf files. For all those reasons I tend to use 3mf files for printing rather than stl files. However, I will show you how to save models in both formats so you can choose (the latest FreeCAD files in the PUMA project – such as those for the CNC stage – are made in the modern (post v.1.0) FreeCAD so may be edited and saved as STL if desired). Generating .3mf files from the models Due to issues with FreeCAD v.1.0 onwards, take the following steps to avoid printing faulty models if using many of the older PUMA models. These steps will also work with

the newer PUMA FreeCAD models: Load the FreeCAD file but do NOT 'recompute' the model as suggested by FreeCAD (and make sure your FreeCAD does not automatically re-compute models on loading). Instead just select the model and export it as a .3mf file by selecting File -> Export (see the figure).

PUMA 3D Printing Guide v1.3 | Page 16 of 362

Generating STL files from the models If you prefer or need to generate STL files instead of 3mf files, you can do so by means of the following steps. However, these will require you to have fully computed models so you may find this option is not available for the older PUMA models (prior to 2025)

due to modern FreeCAD incompatibilities when loading older FreeCAD files. In some cases the files may undergo the ‘recompute’ process without crashing but, in that case, some aspects of the models may be altered making them ‘wrong’. This is why the 3mf file route discussed above is preferred. 1. Load the CAD file into FreeCAD (I used v. 0.18 to illustrate these steps but a later or the latest version may be reuqired to correctly view and edit the latest models). For the

following illustrated examples I have loaded the ‘Z_Motor.FCStd’ file from the PUMA project. 2. Select the 'Mesh Design' Workbench from the drop down selection list on the top button bar of FreeCAD.

PUMA 3D Printing Guide v1.3 | Page 17 of 362

PUMA 3D Printing Guide v1.3 | Page 18 of 362

3. Left-click on the model you want to create a mesh for so as to select it.

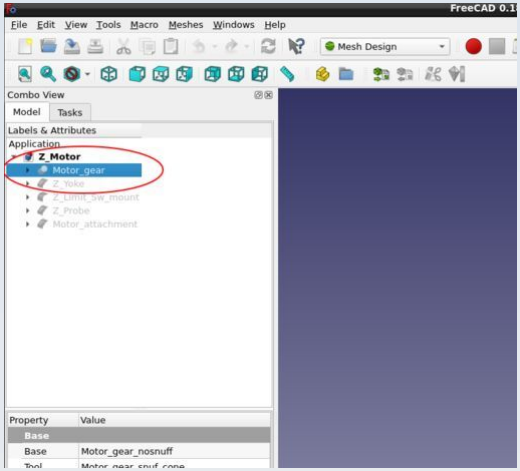
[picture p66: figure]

PUMA 3D Printing Guide v1.3 | Page 19 of 362

4. Go to 'Meshes' -> 'Create mesh from shape ...' to bring up the Tessellation dialogue box.
PUMA 3D Printing Guide v1.3 | Page 20 of 362

5. Select the 'Standard' meshing option set the 'surface deviation' to 0.001 mm and the 'Angular deviation' to 1 degree.
6. Click OK - it may take a while to complete.
These mesh settings may be overly fine for many of the models in that you could probably get away with coarser settings and lower resolution meshes for some models. However I have not experimented to see how low I can go before the models cease to function or cease to fit properly.
PUMA 3D Printing Guide v1.3 | Page 21 of 362

7. When the mesh is generated, right click on the mesh in the 'Model' tab of the combo view and select 'Export Mesh ...' from the drop down menu to save the mesh as an STL file. You might need to rotate the mesh first before export to make it easier to site on the build plate in Cura in the manner required for printing (as will be shown in the illustrations in the rest of this document for each model). Although you can also performs most of those manipulations in Cura itself.
PUMA 3D Printing Guide v1.3 | Page 22 of 362

## Printer and Slicer Software and Settings

This advice relates specifically to printing parts using a Creality Ender 3 printer with ordinary PLA 1.75 mm diameter filament and the Ultimaker Cura slicer software (v. 4.8.0 to v. 4.13.1).
If you use a different printer and / or slicer you would need to explore for yourself what are the most appropriate settings and profiles to use and may also need to modify other aspects of the advice given here.
Note the orientation of models on the print bed as shown in the figures. For some models is probably won’t matter if you use a different orientation but for others is it crucial to functionality that you stick to the orientation shown. My advice therefore is to alwatys use the orientation shown in the figures unless you want to experiment and are happy to risk either failure or suboptimal functionality.
All models are printed with the PUMA custom Cura profile called ‘Flats’ unless otherwise specified (several other PUMA custom Cura profiles are used on occasion and these are available in the GitHub repository). No supports are used unless specified otherwise. None of the Cura in-built build plate adhesion options are used. Where necessary, custom adhesion structures – called ‘adhesins’ – are built into the model and these will need to be trimmed off when the model is complete as part of model post print clean up.
I have only ever printed the parts of this project using super high quality print settings and the highest resolution tessellation meshes. No doubt this is ‘overkill’ for many of the parts but I have not done the practical experimentation required to find out the lowest resolution meshes that will work with the lowest quality / fastest print settings.
I have only ever used standard PLA 1.75 mm filament for printing the parts of this project – although I have used PLA from different suppliers from Creality’s own brand to much cheaper generic filament. With the highest quality branded filaments the prints seem a bit smoother but from a functionality point of view all filaments I have tried give acceptable results. Supports

You don't need supports for screw thread holes up to M4 diameter that are printed horizontally but Cura will try to insert supports for these which is one of the reasons why support advice in some of the models below specifies to use the 'touching build plate only' option (not 'Everywhere'). When supports are enabled the default overhang angle should be set to 67 degrees. For ‘Tree’ supports the default parameters to use are: ‘branch distance’ is 1 mm,

‘branch diameter’ is 2 mm, ‘branch diameter angle’ is 5 degrees and ‘collision resolution’ is 0.2 mm. The ‘branch angle’ for Tree supports may be 40 or 50 degrees depending on the model so this information is provided for each model that required tree supports. If supports are not stated to be required then ensure supports are off – even if it appears (or Cura suggests) that they might be needed. Sometimes this is emphasised

PUMA 3D Printing Guide v1.3 | Page 23 of 362

for models where having supports enabled could cause the print to fail of adversely affect the function of the resulting print.
Some models require specific support blockers. These will be illustrated in the figures. Mesh Errors

Very occasionally for some models Cura will report model errors in the STL mesh and highlight those areas in bright colours. These ‘errors’ are very small and the model slices and prints just fine even with them so they can be ignored. During development I have been able to identify and fix some of those mesh errors in FreeCAD but the very few remaining ones were not obvious – and practically they do not matter for printing with an Ender 3 printer.

PUMA 3D Printing Guide v1.3 | Page 24 of 362

## Post Processing and Aftercare of Prints

I have noticed that PLA prints will shrink a little if exposed to excessive heat post printing and this may distort closely fitting parts and prevent them from functioning adequately. To avoid this, never keep your 3D printed parts on or very near to a radiator and never use a heater, hair dryer or radiator to dry off any parts that may have gotten wet. Leaving parts in a car in the sun may have a similar detrimental heat shrinkage effect.
Some parts, especially closely fitting parts like threads and push fit components may need scraping or light sanding to remove ‘nerds’, ‘zits’ or prominent seams or other imperfections prior to use. It is advised that you allow parts to cool down thoroughly after printing before any such actions (especially sanding) otherwise you may find that you have over-eroded the model and end up with a fit that is too loose. Some 3D printed threads may require ‘training’ if they seem overly tight. This means you screw and unscrew the thread repeatedly to wear it down a bit – this will usually wear down small prominences / defects in the print that lie in the thread channels. This may need to be done gradually (you may not be able to screw a part all the way in at first). After training the thread should fit snugly without being too tight or too loose. Some parts require lubrication – such as the polariser wheel and Z-stage bearings. This will be elaborated on in the construction and usage tutorials. Many thread holes for screws (mostly M2 and M3 sizes but sometimes also up to M6) in many of the parts are printed simply as holes that are slightly too small for the screw and you are expected to cut a thread into the hole by simply screwing the metal screw into the hole. Do this slowly at first concentration on getting the screw perpendicular to

the hole and applying downward pressure. For such joints it is important never to over-tighten the screws in the finished product because you can easily destroy the plastic thread so produced. Also, you should avoid unscrewing and re-screwing in those holes because the thread will wear out eventually (although they can take quite a few repeats before wearing down to a detrimental degree).

PUMA 3D Printing Guide v1.3 | Page 25 of 362

## Aperta Control Console

These are the parts for the PUMA Aperta control console module which provides an advanced interface for the spatial light modulator (SLM). The CAD source models for these files are found in the file PUMA_Aperta.FCStd.

## Resources

Cura calculates the following resources are required to print each model in this chapter:

Model | Time_Hr | Time_Min | PLA_Length(m)
AC_Aperta_base | 2 | 34 | 7.66
AC_Aperta_feet | 0 | 27 | 1.64
AC_Aperta_top | 7 | 52 | 23.88
AC_USB_bottom | 0 | 51 | 2.62
AC_USB_top | 1 | 32 | 4.76
AC_Videhorn | 3 | 2 | 14.14
PUMA 3D Printing Guide v1.3 | Page 26 of 362

## AC_Aperta_base

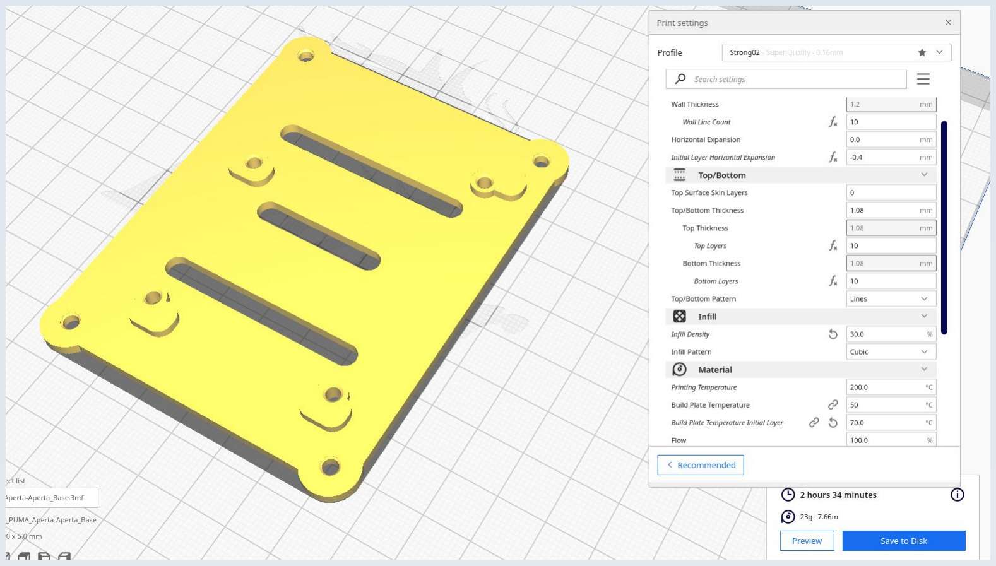
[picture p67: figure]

PUMA 3D Printing Guide v1.3 | Page 27 of 362

## AC_Aperta_feet

See AC_USB_top.

PUMA 3D Printing Guide v1.3 | Page 28 of 362

## AC_Aperta_top

The top is printed with its top surface on the print bed. This needs to have some supports (I use tree supports) but only for three regions: the large curved hollow near the attachment for the PUMA control monitor, the opening for the TFT/SLM cable and the opening for the PARDUS parallel port (PPP) connector. These are shown in the figures. Cura will want to put tiny supports at many other points but these should be blocked because they are not necessary and those supports are so small that they might mis-print and cause problems.

PUMA 3D Printing Guide v1.3 | Page 29 of 362

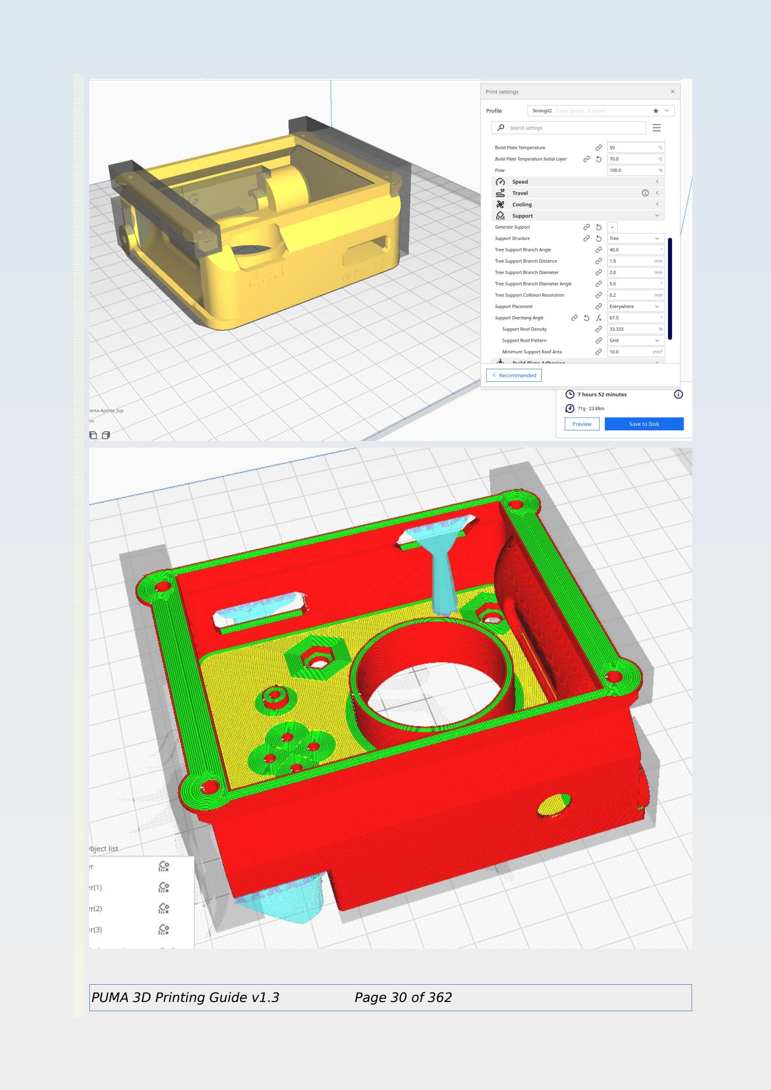
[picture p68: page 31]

PUMA 3D Printing Guide v1.3 | Page 30 of 362

## AC_USB_bottom

See AC_USB_top.

## AC_USB_top

This shows both parts of the USB adapter case and the 4 feet of the Aperta control console being printed together.

PUMA 3D Printing Guide v1.3 | Page 31 of 362

## AC_Videhorn

This figure shows the videhorn being printed together with the retaining ring for the Fresnel lens. This retention ring model is the 'PC_Monitor_lens_retainer' model found in the 'PUMA Control Console' (see that section for more details).

Note that you need supports for this - as shown.

PUMA 3D Printing Guide v1.3 | Page 32 of 362

## AR Projector

These are the parts for the augmented reality (AR) projector module which provides a heads-up-display (HUD) graphical user interface to the user. The CAD source models for these files are found in the file AR_Projector.FCStd.

## Resources

Cura calculates the following resources are required to print each model in this chapter:

AR_Projector | Time_Hr | Time_Min | PLA_Length(m)
AR_Cc_locknut | 0 | 12 | 0.35
AR_Cc_mount_drawtube | 1 | 49 | 6.3
AR_Cc_Retainer | 0 | 7 | 0.28
AR_Cx_Cc_connector | 0 | 28 | 1.16
AR_Cx_Collar | 0 | 11 | 0.36
AR_Cx_Lens_holder | 0 | 32 | 1.97
AR_Clip | 0 | 45 | 1.41
AR_Light_block_filter | 0 | 1 | 0.06
AR_Stay_thumbwheel | 0 | 15 | 0.56
AR_TFT_DrawTube_F | 2 | 59 | 5.33
AR_TFT_Drawtube_sheath | 0 | 18 | 0.87
AR_TFT_LightShield | 0 | 43 | 1.49
AR_TFT_Mount | 1 | 1 | 2.3
AR_Slide_mount | 0 | 59 | 1.91
PUMA 3D Printing Guide v1.3 | Page 33 of 362

## AR_Cc_locknut

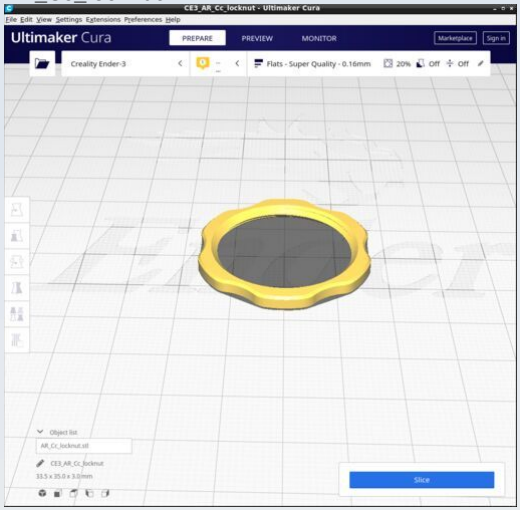
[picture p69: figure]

PUMA 3D Printing Guide v1.3 | Page 34 of 362

## AR_Cc_mount_drawtube

Print with PUMA custom Cura profile ‘P_AR_Tube’

PUMA 3D Printing Guide v1.3 | Page 35 of 362

## AR_Cc_Retainer

PUMA 3D Printing Guide v1.3 | Page 36 of 362

## AR_Clip

Use standard supports (not tree) with overhang of 67 degrees.

PUMA 3D Printing Guide v1.3 | Page 37 of 362

## AR_Light_block_filter

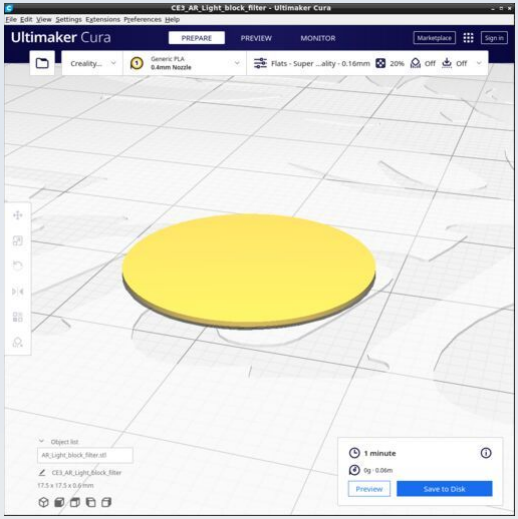
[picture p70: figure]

PUMA 3D Printing Guide v1.3 | Page 38 of 362

## AR_Cx_Cc_connector

PUMA 3D Printing Guide v1.3 | Page 39 of 362

## AR_Cx_Collar

PUMA 3D Printing Guide v1.3 | Page 40 of 362

## AR_Cx_Lens_holder

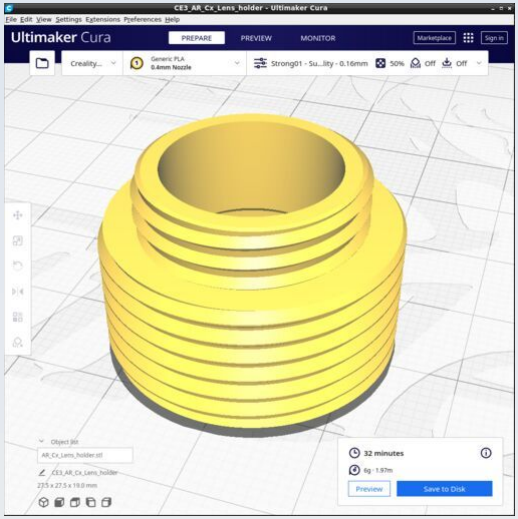
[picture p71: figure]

Print with PUMA custom Cura profile ‘Strong01’

PUMA 3D Printing Guide v1.3 | Page 41 of 362

## AR_Stay_thumbwheel

Use profile ‘Strong01’. No supports.

PUMA 3D Printing Guide v1.3 | Page 42 of 362

## AR_TFT_DrawTube_F

PUMA 3D Printing Guide v1.3 | Page 43 of 362

## AR_TFT_Drawtube_sheath

PUMA 3D Printing Guide v1.3 | Page 44 of 362

## AR_TFT_LightShield

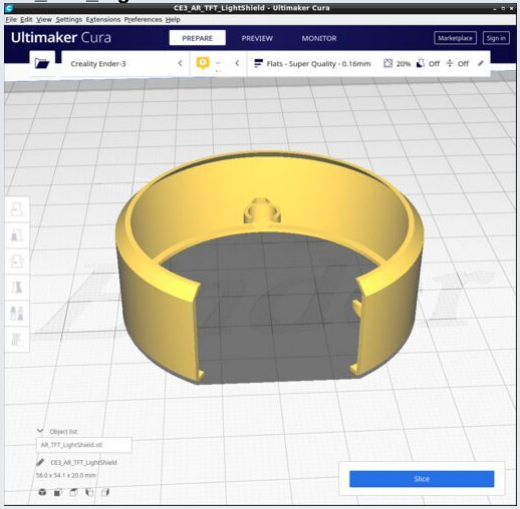
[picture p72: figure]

PUMA 3D Printing Guide v1.3 | Page 45 of 362

## AR_TFT_Mount

PUMA 3D Printing Guide v1.3 | Page 46 of 362

## AR_Slide_mount

PUMA 3D Printing Guide v1.3 | Page 47 of 362

## Binocular Head

These are the 3D printed parts for the binocular head module. The CAD source models for these files are found in the file Binocular.FCStd.

## Resources

Cura calculates the following resources are required to print each model in this chapter:

Binocular_Head | Time_Hr | Time_Min | PLA_Length(m)
BN_Cap_spacer_bolt_arm | 0 | 21 | 0.77
BN_Cap_spacer_nut_arm | 0 | 22 | 0.95
BN_CM_BB_Cover | 0 | 31 | 1.13
BN_CM_Tube_short_c_adhesin | 0 | 41 | 1.69
BN_EM_Cover | 0 | 21 | 0.87
BN_MB_Shim | 0 | 5 | 0.08
BN_MBT_Cap | 0 | 24 | 1
BN_MBT_Ring | 0 | 21 | 0.64
BN_MB_Tube | 1 | 50 | 3.68
BN_MB_Tube_spacer_2p5mm | 0 | 12 | 0.28
BN_Mirror_mount_bottom | 1 | 0 | 1.51
BN_Mirror_mount_top_ocular | 1 | 31 | 2.84
BN_Ocular_spacer_ring_0p32 | 0 | 2 | 0.06
BN_Ocular_Base_thread_L | 0 | 35 | 0.86
BN_Ocular_Base_thread_R | 0 | 35 | 0.86
BN_Outlet_lower_spacer | 0 | 0 | 0.02
BN_Outlet_upper | 1 | 42 | 2.72
BN_Splitter_block | 2 | 4 | 3.35
BN_Splitter_support | 0 | 1 | 0.02
PUMA 3D Printing Guide v1.3 | Page 48 of 362

## BN_Cap_spacer_bolt_arm

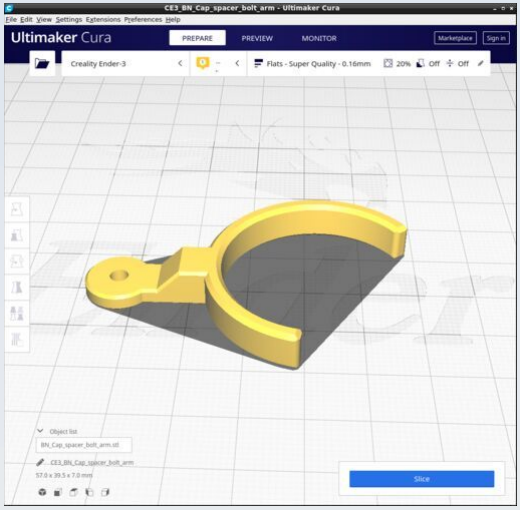
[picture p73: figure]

PUMA 3D Printing Guide v1.3 | Page 49 of 362

## BN_Cap_spacer_nut_arm

Use the Condenser profile (including its support settings).

PUMA 3D Printing Guide v1.3 | Page 50 of 362

## BN_CM_BB_Cover

PUMA 3D Printing Guide v1.3 | Page 51 of 362

## BN_CM_Tube_short_c_adhesin

PUMA 3D Printing Guide v1.3 | Page 52 of 362

## BN_EM_Cover

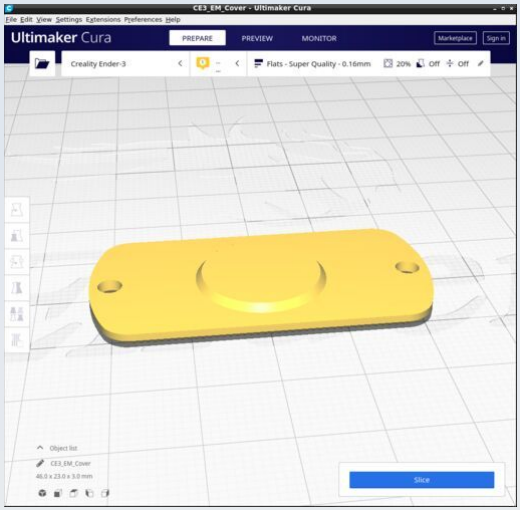
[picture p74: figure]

PUMA 3D Printing Guide v1.3 | Page 53 of 362

## BN_MB_Shim

PUMA 3D Printing Guide v1.3 | Page 54 of 362

## BN_MBT_Cap

PUMA 3D Printing Guide v1.3 | Page 55 of 362

## BN_MBT_Ring

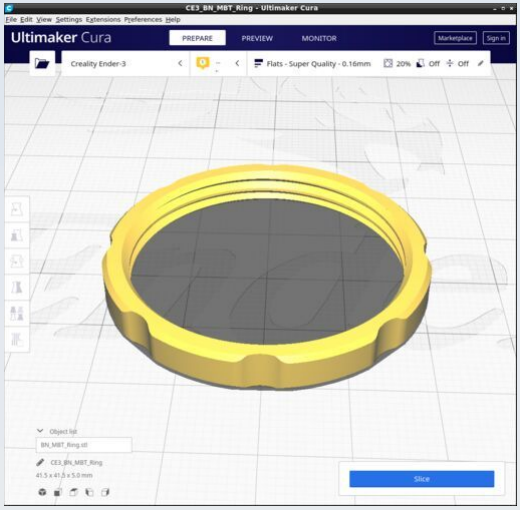
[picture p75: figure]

PUMA 3D Printing Guide v1.3 | Page 56 of 362

## BN_MB_Tube

PUMA 3D Printing Guide v1.3 | Page 57 of 362

## BN_MB_Tube_spacer_0p48mm

PUMA 3D Printing Guide v1.3 | Page 58 of 362

## BN_MB_Tube_spacer_2p5mm

This is just one example from a range of MB_Tube_spacers of various thicknesses.

PUMA 3D Printing Guide v1.3 | Page 59 of 362

## BN_Mirror_mount_bottom

Select suports 'touching build plate only' (not 'Everywhere').

PUMA 3D Printing Guide v1.3 | Page 60 of 362

## BN_Mirror_mount_top_ocular

Select suports 'touching build plate only' (not 'Everywhere').

PUMA 3D Printing Guide v1.3 | Page 61 of 362

## BN_Ocular_spacer_ring_0p32

Use 'Top/bottom pattern'='Concentric' in the Top/Bottom' settings

PUMA 3D Printing Guide v1.3 | Page 62 of 362

## BN_Ocular_Base_thread_L

Select suports 'touching build plate only' (not 'Everywhere').

PUMA 3D Printing Guide v1.3 | Page 63 of 362

## BN_Ocular_Base_thread_R

Select suports 'touching build plate only' (not 'Everywhere').

PUMA 3D Printing Guide v1.3 | Page 64 of 362

## BN_Outlet_lower_spacer

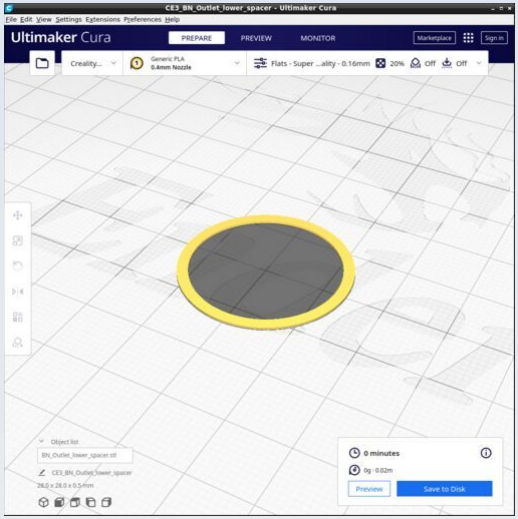
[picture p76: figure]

PUMA 3D Printing Guide v1.3 | Page 65 of 362

## BN_Outlet_upper

Use supports of 'Tree' type 'touching build plate only' (not 'Everywhere') and change the default for 'tree support branch distance' from 1.0 mm to 0.2 mm.

PUMA 3D Printing Guide v1.3 | Page 66 of 362

## BN_Splitter_block

Select suports 'touching build plate only' (not 'Everywhere').

PUMA 3D Printing Guide v1.3 | Page 67 of 362

## BN_Splitter_support

PUMA 3D Printing Guide v1.3 | Page 68 of 362

## CNC-Stage

These are the parts for making the CNC precision motorised XYZ stage. The CAD source models for these files are found in the file CNC_Stage.FCStd.
All models are printed with the basic Cura profile ‘Strong02’ (10 wall layers and 10 layers top and bottom) and most are printed with an infill of 30%. Details of any modifications to this and any supports / support blockers will be provided with each model.
Location of the models Due to GitHub placing a 25Mb limit on file sizes, I have had to split the models into 3 files. Each file contains the following model groups and model: File: CNC_Stage_1.FCStd Group: PSU

PSU_CableFixture_front PSU_DC_CableCover PSU_Mains_CableCover PSU_Peg_Leg Group: Arduino

Ardu_bus_bar_mount Ardu_Bus_Clip_set Ardu_M3_Washer Group: X_Axis X_ATLAS_M6_Axle_holder X_ATLAS_base

X_Lim_Sarcoph_L X_Lim_Sarcoph_R X_NEMA11_Bracket X_NEMA11_Counter_weight X_NEMA11_CW_Hopper

X_Probe X_Probe_Housing_L X_Probe_Housing_R X_Probe_shim XY_ATLAS_Spring_well_washer_1p5mm

PUMA 3D Printing Guide v1.3 | Page 69 of 362

XY_ATLAS_Spring_well_washer_2p0mm XY_ATLAS_Spring_well_washer_2p5mm XY_ATLAS_Spring_well_washer_3p0mm XY_NEMA11_Undertable_Support

File: CNC_Stage_2.FCStd
Group: Y_Axis
Y_ATLAS_Axle_pair
Y_ATLAS_base Y_Lim_Sarcoph_Susp_B Y_Lim_Sarcoph_Susp_F Y_NEMA11_Bracket Y_Probe_Susp_Nemesh

Y_Suspension_platform_B Y_Suspension_platform_F Group: Z_Axis Z_Coupler Z_Lim_Attachment Z_Lim_Back_baffle

Z_Lim_Probe Z_M4_small_washer Z_Mount Z_N11_Syringe_body Z_N11_Syringe_cover

Z_N11_Syringe_Gearbox_plunger Z_N11_Syringe_mount Group: Frame F_Ardu_strut_BL F_Ardu_strut_BR

F_Ardu_strut_TL F_Ardu_strut_TR F_DM3_Mount F_DPST_to_2020 F_OM_QR_Plate F_Overmount

PUMA 3D Printing Guide v1.3 | Page 70 of 362

F_RAMPS_clamp_Left
F_RAMPS_clamp_Right
F_UM_Opt_gripper
F_UM_Opt_Gripper_washer
F_UM_Opt_to_QR_F
F_Undercarriage_platform
Group: Sample_holder
Sam_Counter_weight
Sam_Pincer_Extn1_L Sam_Pincer_Extn1_R Sam_Pincer_Extn2_L Sam_Pincer_Extn2_R Sam_Presser_wings

Sam_Spring_arm_assy Sam_Stage_Top File: CNC_Stage_3.FCStd Group: BaseBoard BB_Jig_Back_Left

BB_Jig_Back_Measure BB_Jig_Back_Right BB_Jig_Front_Left BB_Jig_Front_Measure BB_Jig_Front_Right

BB_Jig_Left_Measure BB_Jig_Right_Measure BB_Jig_Undercarriage BB_Jig_XYTable BB_Jig_Y_Lim

Group: Shields SD_2020_End_cap SD_2020_Protector SD_Aft_clip SD_Aft_Hole_cover SD_Aft_Left

PUMA 3D Printing Guide v1.3 | Page 71 of 362

SD_Aft_Mid
SD_Aft_Right
SD_Aft_Rivet_block
SD_DIN_End_Protector
SD_DIN_Foot_Protector
SD_Dorsal_Key_head
SD_Dorsal_Key_key
SD_Dorsal_Key_main
SD_Dorsal_Key_wedge SD_Dorsal_L SD_Dorsal_M SD_Dorsal_R SD_Dorsal_Rivet_plate

SD_Dorsal_suture SD_Forward_L SD_Forward_R SD_Forward_Rivet_handle_1 SD_Forward_Rivet_handle_2 SD_Forward_Rivet_lock

SD_Forward_Rivet_tool SD_Forward_suture SD_Lateral_Left SD_Lateral_Right SD_Letters_CNC

SD_Letters_PUMA SD_T_nut_positioner SD_XMotor_cover_L SD_XMotor_cover_R

PUMA 3D Printing Guide v1.3 | Page 72 of 362

## Resources

Cura 4.13.1 calculates the following resources are required to print each model in this chapter:

CNC-Stage | Time_Hr Time_Min PLA_Length(m)
CN_Ardu_bus_bar_mount | 7 | 29 | 20.74
CN_Ardu_Bus_Clip_set | 4 | 13 | 6.1
CN_Ardu_M3_Washer | 0 | 1 | 0.02
CN_BB_Jig_Back_Left | 5 | 10 | 12.8
CN_BB_Jig_Back_Measure | 1 | 13 | 3.02
CN_BB_Jig_Back_Right | 5 | 10 | 12.8
CN_BB_Jig_Front_Left | 4 | 57 | 12.47
CN_BB_Jig_Front_Measure | 0 | 17 | 0.87
CN_BB_Jig_Front_Right | 4 | 57 | 12.47
CN_BB_Jig_Left_Measure | 1 | 22 | 3.6
CN_BB_Jig_Right_Measure | 1 | 22 | 3.6
CN_BB_Jig_Undercarriage | 4 | 49 | 12.12
CN_BB_Jig_XYTable | 5 | 33 | 13.98
CN_BB_Jig_Y_Lim | 0 | 38 | 2.09
CN_F_Ardu_strut_BL | 1 | 49 | 5.8
CN_F_Ardu_strut_BR | 1 | 49 | 5.8
CN_F_Ardu_strut_TL | 1 | 49 | 5.8
CN_F_Ardu_strut_TR | 1 | 49 | 5.8
CN_F_DM3_Mount | 2 | 12 | 6.32
CN_F_DPST_to_2020 | 2 | 22 | 5.89
CN_F_OM_QR_Plate | 9 | 43 | 27.37
CN_F_Overmount | 9 | 33 | 26.48
CN_F_RAMPS_clamp_Left | 1 | 35 | 4.2
CN_F_RAMPS_clamp_Right | 1 | 35 | 4.2
CN_F_UM_Opt_gripper | 1 | 42 | 4.61
CN_F_UM_Opt_Gripper_washer | 0 | 3 | 0.16
CN_F_UM_Opt_to_QR_F | 2 | 40 | 7.81
CN_F_Undercarriage_platform | 8 | 36 | 23.99
PUMA 3D Printing Guide v1.3 | Page 73 of 362

CN_PSU_CableFixture_front | 9 | 1 | 29.11
CN_PSU_DC_CableCover | 0 | 32 | 1.66
CN_PSU_Mains_CableCover | 1 | 1 | 2.99
CN_PSU_Peg_Leg | 0 | 9 | 0.3
CN_Sam_Counter_weight | 1 | 6 | 3.15
CN_Sam_Pincer_Extn1_L | 0 | 52 | 2.3
CN_Sam_Pincer_Extn1_R | 0 | 52 | 2.3
CN_Sam_Pincer_Extn2_L | 1 | 24 | 3.92
CN_Sam_Pincer_Extn2_R | 1 | 24 | 3.94
CN_Sam_Presser_wings | 0 | 53 | 2.47
CN_Sam_Spring_arm_assy | 6 | 1 | 15.43
CN_Sam_Stage_Top | 11 | 0 | 28.98
CN_SD_2020_End_cap | 0 | 13 | 0.46
CN_SD_2020_Protector | 0 | 23 | 0.9
CN_SD_Aft_clip | 0 | 5 | 0.07
CN_SD_Aft_Hole_cover | 0 | 34 | 1.84
CN_SD_Aft_Left | 16 | 13 | 67.98
CN_SD_Aft_Mid | 14 | 55 | 54.11
CN_SD_Aft_Right | 16 | 12 | 67.98
CN_SD_Aft_Rivet_block | 0 | 9 | 0.39
CN_SD_DIN_End_Protector | 0 | 20 | 0.86
CN_SD_DIN_Foot_Protector | 0 | 48 | 2.3
CN_SD_Dorsal_Key_head | 0 | 10 | 0.38
CN_SD_Dorsal_Key_key | 0 | 7 | 0.35
CN_SD_Dorsal_Key_main | 0 | 4 | 0.1
CN_SD_Dorsal_Key_wedge | 0 | 0.4 | 0.01
CN_SD_Dorsal_L | 15 | 51 | 47.81
CN_SD_Dorsal_M | 8 | 40 | 29.69
CN_SD_Dorsal_R | 15 | 56 | 48.14
CN_SD_Dorsal_Rivet_plate | 0 | 40 | 2.1
CN_SD_Dorsal_suture | 0 | 16 | 0.68
CN_SD_Forward_L | 3 | 50 | 11.71
CN_SD_Forward_R | 3 | 52 | 11.72
PUMA 3D Printing Guide v1.3 | Page 74 of 362

CN_SD_Forward_Rivet_handle_1 | 0 | 4 | 0.1
CN_SD_Forward_Rivet_handle_2 | 0 | 4 | 0.1
CN_SD_Forward_Rivet_lock | 0 | 9 | 0.28
CN_SD_Forward_Rivet_tool | 0 | 3 | 0.12
CN_SD_Forward_suture | 0 | 40 | 1.86
CN_SD_Lateral_Left | 22 | 47 | 78.26
CN_SD_Lateral_Right | 22 | 30 | 78.23
CN_SD_Letters_CNC | 0 | 11 | 0.52
CN_SD_Letters_PUMA | 0 | 15 | 0.74
CN_SD_T_nut_positioner | 0 | 4 | 0.07
CN_SD_XMotor_cover_L | 9 | 2 | 36.4
CN_SD_XMotor_cover_R | 9 | 2 | 36.4
CN_X_ATLAS_base | 4 | 0 | 9.3
CN_X_ATLAS_M6_Axle_holder | 0 | 55 | 2.03
CN_X_Lim_Sarcoph_L | 2 | 35 | 7.11
CN_X_Lim_Sarcoph_R | 2 | 30 | 7.12
CN_X_NEMA11_Bracket | 9 | 41 | 21.55
CN_X_NEMA11_Counter_weight | 10 | 32 | 25.04
CN_X_NEMA11_CW_Hopper | 3 | 27 | 11.69
CN_X_Probe | 0 | 26 | 1.04
CN_X_Probe_Housing_L | 0 | 53 | 2.77
CN_X_Probe_Housing_R | 0 | 54 | 2.77
CN_X_Probe_shim | 0 | 2 | 0.1
CN_XY_ATLAS_Spring_well_washer_1p5mm | 0 | 3 | 0.05
CN_XY_ATLAS_Spring_well_washer_2p0mm | 0 | 3 | 0.06
CN_XY_ATLAS_Spring_well_washer_2p5mm | 0 | 3 | 0.08
CN_XY_ATLAS_Spring_well_washer_3p0mm | 0 | 3 | 0.09
CN_Y_ATLAS_Axle_pair | 2 | 18 | 5.56
CN_Y_ATLAS_base | 10 | 2 | 25.27
CN_XY_NEMA11_Undertable_Support | 0 | 34 | 1.72
CN_Y_Lim_Sarcoph_Susp_B | 4 | 36 | 12.35
CN_Y_Lim_Sarcoph_Susp_F | 4 | 36 | 12.35
CN_Y_NEMA11_Bracket | 9 | 7 | 20.82
PUMA 3D Printing Guide v1.3 | Page 75 of 362

CN_Y_Probe_Susp_Nemesh | 3 | 53 | 9.31
CN_Y_Suspension_platform_B | 0 | 36 | 1.97
CN_Y_Suspension_platform_F | 0 | 36 | 1.97
CN_Z_Coupler | 0 | 37 | 2.2
CN_Z_Lim_Attachment | 2 | 23 | 6.44
CN_Z_Lim_Back_baffle | 0 | 33 | 0.62
CN_Z_Lim_Probe | 0 | 16 | 0.6
CN_Z_M4_small_washer | 0 | 0.4 | 0.02
CN_Z_Mount | 10 | 17 | 28.73
CN_Z_N11_Syringe_body | 6 | 11 | 14.84
CN_Z_N11_Syringe_cover | 0 | 42 | 1.66
CN_Z_N11_Syringe_Gearbox_plunger | 2 | 45 | 7.09
CN_Z_N11_Syringe_mount | 8 | 26 | 23.77
PUMA 3D Printing Guide v1.3 | Page 76 of 362

## CN_PSU_CableFixture_front

PUMA 3D Printing Guide v1.3 | Page 77 of 362

## CN_PSU_DC_CableCover

PUMA 3D Printing Guide v1.3 | Page 78 of 362

## CN_PSU_Mains_CableCover

PUMA 3D Printing Guide v1.3 | Page 79 of 362

## CN_PSU_Peg_Leg

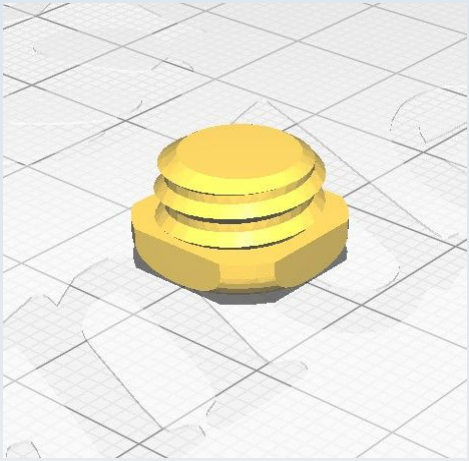
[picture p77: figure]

PUMA 3D Printing Guide v1.3 | Page 80 of 362

## CN_Ardu_bus_bar_mount

PUMA 3D Printing Guide v1.3 | Page 81 of 362

## CN_Ardu_Bus_Clip_set

Note: Printing these as a set is convenient, time-saving and allows for better print-bed adhesion but you could print the individual clips in this set separately if you want to. They must be orientated on the print bed on their ‘side’ as shown in this image, even if

only printing one alone.

PUMA 3D Printing Guide v1.3 | Page 82 of 362

## CN_Ardu_M3_Washer

Use ‘Concentric’ for Top/bottom pattern.

PUMA 3D Printing Guide v1.3 | Page 83 of 362

## CN_X_ATLAS_base

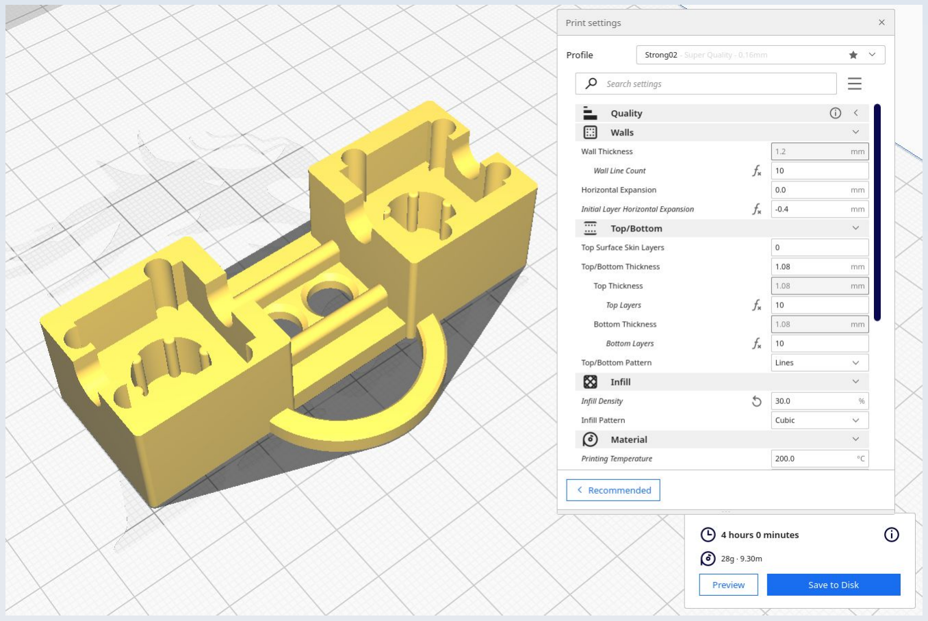
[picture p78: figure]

PUMA 3D Printing Guide v1.3 | Page 84 of 362

## CN_X_ATLAS_M6_Axle_holder

PUMA 3D Printing Guide v1.3 | Page 85 of 362

## CN_X_Lim_Sarcoph_L

This uses tree supports ‘everywhere’ as shown in the top inset.

PUMA 3D Printing Guide v1.3 | Page 86 of 362

## CN_X_Lim_Sarcoph_R

This also uses tree supports (as for CN_X_Lim_Sarcoph_L) but, in addition, there is a support blocker stopping the supports going in the M2 holes and limit switch alcove, as shown.

PUMA 3D Printing Guide v1.3 | Page 87 of 362
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

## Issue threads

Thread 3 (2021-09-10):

### ISSUE TITLE
Roadmap

### ISSUE THREAD

**Issue by luzpaz** [TadPath/PUMA#3]
Are there more features on the horizon?

**Comment by TadPath** [comment]
Definitely!

- A dedicated infinity adapter module that will allow the use of the SLM in the back focal plane of the objective as well as allow the use of infinity objectives from all major microscope manufacturers (as well as generics).
- I am planning to make in vitro cell culture attachment module for the stage to observe living cells.
- 3D imaging set-ups - including a robotic XYZ controller for the stage and free deconvolution software.
- More detailed 'How To' documentation. I have a video ready to relaase - just working on the subtitles now - which is the first full 'How To' guide that shows how to build the PUMA stage from scratch. It will be made public on YouTube soon.
- More demo experiment videos to teach people how to upgrade the scope and how to use its various features with practical examples.
- As @sandorkonya says, development of software for PC / Raspberry Pi to interface the SLM and AR HUD. Just because PUMA is protable doesn't mean it can't also be used as a benchtop instrument as well. In fact, the XYZ stage controller for 3D imaging will need to use a proper computer I think (RPi at least) - Arduino will not cut it.
- There is a lot more I have in mind - but how much of this is actually realised will depend on the amount of uptake and support is shown for the project from the community. I watch the response to my YouTube channel and GitHub repository and other correspondence and continually assess that. I am not big on social media so I must rely on others to spread the word if they like what I am doing to drum up support.

**Comment by luzpaz** [comment]
Awesome, perhaps tracking it using https://github.com/TadPath/PUMA/projects ?

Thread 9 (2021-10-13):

### ISSUE TITLE
Collector_mirror_block clamping problem

### ISSUE THREAD

**Issue by DerFetzer** [TadPath/PUMA#9]
**Describe the bug**
The holes for the thumbscrews in the Collector_mirror_block are not going through the shell.
Is this a design choice and the screw is supposed to deform the shell for the clamping effect or are they missing?

**Expected behavior**
I expected holes like in M3_Adjustment_ring_Kohler.

**Screenshots**
![grafik](https://user-images.githubusercontent.com/11207998/137172262-3708dbce-88bd-434f-8793-6809d503a3b0.png)

**Comment by TadPath** [comment]
Thank you for considering the project and asking the question.The answer is no, this is not a bug or issue. This is a design implementation as I will now explain. In both models the slot you see is to accept an M3 nut which furnishes the thread to drive the screw through to grip the articulating part (I assume you already got that). However, the two models do 'gripping' in different ways for different reasons. DI_M3_Adjustment_ring_Kohler passes the screw end directly onto the indented ring on the outer surface of the DI_LC_Adjust_collar and grips it that way - you need the little screw end to grip directly into this little channel to allow maximum angle adjustment with this small diameter part. The hole in DI_Collector_mirror_block pass the metal end of the M3 screw onto the 'blind' plate of plastic and deforms that blind plate of plastic to push it inwards. It is this deformed plastic which grips the inner part (DI_Cnd_to_UC). This is to avoid the little screw end from creating indentations on DI_Cnd_to_UC if it were applied directly and so help allow fine adjustment in alignment of the Köhler system. I haven't done the Köhler illuminator video tutorial yet so you could not have known this. Thanks for considering the project. Please note that I have set up a Twitter feed @Paul_Tadrous - where you will see some snippets and news items about PUMA. If you have a Twitter account, please consider re-tweeting some of my tweets to help reach more people. I welcome input from the community.

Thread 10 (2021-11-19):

### ISSUE TITLE
Eccentric_Tensioners missing the .stl fileextension in the stl BOM list

### ISSUE THREAD

**Issue by t0b4cc0** [TadPath/PUMA#10]
Hi! I am working on building a PUMA microscope. I am also working on a configurator that just prints out a BOM, stls, links etc with build lists.

I noticed that in the stl file list the 

FG_Eccentric_Tensioner_Top
FG_Eccentric_Tensioner_Bottom
FG_Eccentric_Tensioner_Pulley_c_adhesin

are missing the ".stl" file extension

As is like to keep this automated I wonder is that intentional and i have to work with it or just an oversight?

It seems like all things that are actual .stl files have the stl file extension. and the other things in this list are just headings grouping the items right?

EDIT: also AR_Clip_lock has no stl file ending. I can easily deal with this, i just wonder why this is the case.

**Comment by TadPath** [comment]
Hello. Thanks for pointing these out. You are correct, the lack of stl extension is simply an oversight on my part. I will fix this in the next commit for the sake of consistency. However, In the longer term future I am not sure if I should keep the stl extensions as some people prefer to work with 3mf files instead and, anyway, I don't provide actual stl files I provide FreeCAD models and people are free to choose what kind of print-ready format they generate from it. So maybe it would be better for the long term applicability of your program if you bear in mind that this extension could change or be omitted in future versions. I look forward to seeing your configurator in action!

**Comment by t0b4cc0** [comment]
Nice thank you. I just didnt know if there was something special to these objects. It works now without relying on the extension.

I will say that its a bit helpful atleast to have the extension to know that this is actually one file that is printable, and easy interchangable with whatever file extension I choose for a build.

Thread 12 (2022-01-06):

### ISSUE TITLE
Missing files?

### ISSUE THREAD

**Issue by liquidbear99** [TadPath/PUMA#12]
The FreeCAD folder does not contain all of the files. Ex. For making the stage you need the base plate, focus plate, etc but only the focus plate is in the FreeCAD folder.

**Comment by TadPath** [comment]
Hello. Thanks for raising the issue. I have just downloaded the Stage.FCStd file from the repo to check. I can confirm that all the parts are there. It is just that not all of them are marked as 'visible'. You should see on the left hand panel the 'Base_plate' and 'Articulation' models are shaded out to indicate they are not currently visible. Just left click (once) on the model you want to see (to select it) and press space bar to toggle visibility on/off. I do not set all parts to visible in the files because this can overwhelm graphics card and slow up rendering. I will close the issue as there are no missing files / models I can see but do open another issue if you think a model is actually missing (as opposed to not currently visible). Please note that some models may also appear a bit odd depending on your graphics card settings (e.g. missing a wall) but the STL mesh you generate should be complete and printable (even if the printer complains of a mesh error) - you can check before you print using your slicer nozzle emulator to see if there are any real issues prior to printing. Thanks.

**Comment by liquidbear99** [comment]
Thanks! That fixed it! I'm new to FreeCAD, sorry for taking your time away.

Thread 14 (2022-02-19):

### ISSUE TITLE
Question: Would this specific model X-Y slide holder fit the puma scope? I noticed there was not one listed in the non-printed-parts.

### ISSUE THREAD

**Issue by liquidbear99** [TadPath/PUMA#14]
Hello, I have just built the basic microscope and am looking to upgrade it a bit! I noticed there was no recommended/example x-y slide holder and it may be worth adding this to the excel document if it would fit.

Do you know if this would fit?
https://www.aliexpress.com/item/1904300031.html?spm=a2g0o.cart.0.0.40f33c00HrxRq6&mp=1

**Comment by TadPath** [comment]
Nice to hear you made one - hope the experience and end result are satisfying. Do post on social media your experiences to help raise awareness. Re upgrades - there is too much detail to write about so I put these in the videos as I make them. This XY will fit the holes in the stage but the curved arm will be too long - you would need to truncate it in a correct way to avoid it snagging on the front focus post (truncate it in the wrong way and you loose functionality). I will provide details when I do the video on stage accessories. This type also needs correct application of the XY stabiliser - again there are important details that will need to wait for the video. As stated in the intro github readme, upgrade modules may get revised while I make tutorials so be aware that some models and instruction may change by then (for the better). So I update all Github docs (Excel, FreeCAD files, 3DPrinting guide) for each upgrade as I make each tutorial. Thanks for your interest in the project.

**Comment by liquidbear99** [comment]
No worries! I appreciate the effort on this project. It is quite amazing the quality that I have from just the base model. I did also want to recommend you visit the link provided here for the 23mm convex lens. This link is the same product as the ebay one you provide, but is cheaper on Aliexpress. https://www.aliexpress.com/item/1924222603.html?spm=a2g0o.order_list.0.0.21ef1802SxBDkC

On a side note, if there is any way I could become more involved in development or helping this project let me know. I am thinking about writing a review article on my assembly process and concerning the possible medical implications of this device even though it holds no formal certification (I am a current medical student).

**Comment by TadPath** [comment]
Thanks. If you want to contact me to discuss the project you can use my doctors.org.uk email (the one in the J. Microsc. paper - it will be more convenient for me). BTW you should read the J Microsc. article if you have not done so already.
As a medical student I don't want to distract you from your studies - I dropped all contact with computers and programming when I went to med school in the 1980s to concentrate on my studies but I suppose things are different now. You can help simply by spreading the word on social media and among your peers and tutors. A review article sounds like a good idea and hopefully you will get it published but it sounds like an awful lot of work.
The lens that is bugging me right now is the 30 mm lens because it has come to my attention that there are various 'shapes' available from different sellers so I left a note in the video description of the Abbe condenser video to advise people which to look out for but I am working on that a bit more.

**Comment by liquidbear99** [comment]
Super, I just requested it the other day from our library and I have plans to read it in the near future!

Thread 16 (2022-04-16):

### ISSUE TITLE
Update for URLs in BOM

### ISSUE THREAD

**Issue by UlfWetzker** [TadPath/PUMA#16]
I found a few parts in the Non_Printed_Parts sheet of the PUMA_Bill_of_Materials.xls whose URLs are no longer accurate.

Pages that no longer exist:
Row 116: Polarising film for polariser 0.7 mm thick
Row 117: Polarising film for analyser 0.13 mm thick

I have been looking for other polarizing films of this thickness. Unfortunately, I could not find anything through the search of Aliexpress. Is the thickness of the polarizing filters very important or can I take other thicknesses here? In general, there are many polarizing films on Aliexpress, but whether these can be used is questionable.

Products that are no longer available:
Row 111: Mirror_2cm_square_first_surface_full_2mm_thick
Row 114: Beamsplitter_glass_2cm_square_1.1mm_thick

The Bohroptics Aliexpress shop is apparently on vacation. Maybe the products will be available again soon.

If alternative sources for these parts are known, I would appreciate an update of the Excel file.

**Comment by TadPath** [comment]
Hello. Thanks for the heads up. I have updated the link to the polariser sheet examplar supplier - it seems they just switched address link for some reason. Regarding thickness - it must be <= 0.9 mm to fit in the filter trays for PUMA. For use with the DI_Uber_pol it must be as thin as possible - but the exact thickness is not crucial. I mentioned this in some new notes added to the BOM spreadsheet.
A quick search on AE found an alternative supplier of the 2 cm square first surface mirror here (but I am NOT recommending them - they are more expensive and I haven't tried them out - just saying if you shop around you should find these generic products across a number of stores - it may take some time and effort searching using the correct search key words, etc.): https://www.aliexpress.com/item/4000582254851.html
If any product proves to be unavailable in the long term I will just have to see if I can make a modified model to accept whatever is available but I think availability will fluctuate over time for any single item.

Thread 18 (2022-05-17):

### ISSUE TITLE
Prefer additive manufacturing format (amf) to STL

### ISSUE THREAD

**Issue by plaes** [TadPath/PUMA#18]
Current 3D Printing guide suggests using STL files as intermediate format for 3D-printing and although it works, this format has various shortcomings that have been addressed in the [AMF](https://en.wikipedia.org/wiki/Additive_manufacturing_file_format). AMF is also an open standard.

FreeCAD also supports exporting AMF, just make exportable object (or body) active and from menu select File -> Export and select "Additive Manufacturing Format (*.amf)" as a type. This would allow to clean up the whole mesh preparation process from the documentation.

Although my 3D-printing process does not involve Cura (I'm using PrusaSlicer), I'm pretty sure it's also supported there.

**Comment by TadPath** [comment]
Yes - I agree that other formats may be better for some uses which is one of the reasons I chose not to publish STLs but full FreeCAD models (so people can chose which format they prefer for printing, as well as to make the scope easier to customise). Cura supports AMF files as well. I use the example of STL in my docs only because it is very commonly used in the home/school/college 3D print community. I myself have not tried using AMF though so I don't have personal experience of it. Perhaps I can put a note about alternative formats in the 3D Printing Guide for completeness when I next update it. Thanks.

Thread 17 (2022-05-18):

### ISSUE TITLE
Quick start guide?

### ISSUE THREAD

**Issue by InnerLive** [TadPath/PUMA#17]
Is there anything like a quick start guide so that I know what I need to print to build configuration 1 myself?
Maybe I missed this, but I'm a little lost. What are the minimum parts I need to print?
And preferably the matching hardware that needs to be purchased.

Thanks for the great work!

**Comment by TadPath** [comment]
Not yet as such - but I realise I need to do this because you are not the first to ask. In the mean time the best way to get started is a combination of the following:

1. Get familiar with the Bill_of_Materials spreadsheet - this has a full list of the specific parts (3D printed and purchased hardware) you need for each module and for each of 3 typical configurations of completed microscope (a 'configuration' is made up of a collection of modules). It also has some example URLs where you can purchase specific non-printed parts on AliExpress and eBay, etc.
2. Get familiar with the 3D printing guide PDF - read the intro pages and look at a few of the models pages.
The Foundation Scope user manual PDF is freely available for download from the Optarc.co.uk site - that may also help.
3. Once you have seen these docs you can begin by looking at the videos on 'How to Build the Stage ...', then 'Z-Stage II - Troubleshooting and maintenance'.
4. Once you have built a working stage you have done most of the work needed to make a PUMA microscope. To finish off just see the video on 'How to Build a Foundation scope' - and you should be done. The 'Field strip' and 'Assembly' videos will also be useful watching at this stage. The rest are all about various upgrades and add-ons (and more videos are on the way!)

All the best!

**Comment by TadPath** [comment]
If you see the BoM spreadsheet there is a worksheet near the end called 'CF_Monocular_Mirror_Scope' (this is the simplest 'Foundation scope' config). In the 'Modules' column of that worksheet it lists the modules you need to build for that config. So it currently shows this list:
Stage
Legs_short
Stage_clips
Mirror_Simple
Objective_x40 [Note: this is a typo - it should be x4 not x40 - I will fix it]
Filterblock_simple
Monocular_head
Ocular_lens

Each member of the above list refers to a worksheet in the same spreadsheet which you need to refer to to get the parts to print. For example, 'Stage' refers to the worksheet called: 'MD_Stage' and that worksheet shows you all the 'STL' files you need to print to build that module plus all the non-printed parts you need to get. So, to get everything you need to print and all other hardware you need for a complete scope, just go down the above list and see the 'MD_' module worksheet for each one.
Please see the 3D Print guide PDF for each model before printing to see if there are any special requirements - orientation on the build plate should be as shown in the picture, supports, etc. should be as for the Cura profile for the model (in general use the 'Flats' profile unless specified otherwise. You can download the profiles from the 3D printing part of this GitHub. If you don't use Cura or Ender3 it will be up to use to devise a suitable 'equivalent' profile for your slicer/printer but you can (and I advise should) use the Cura profiles I provide as a template/guide for that.
My videos will show you what to do with all the parts to put them together - this is important because the correct assembly technique is not obvious from looking at the parts.
The stage is the single most complex thing so perhaps before you print all parts for a whole microscope, just attempt to build the stage and see how it goes. If you can get a working stage, the other stuff should be relatively easy and quick to add.

**Comment by InnerLive** [comment]
I have cross-read the PDF already. It looks very well done and comprehensive! I will try my luck as soon as possible.
Thanks a lot!

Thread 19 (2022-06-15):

### ISSUE TITLE
cannot dowload valid zip or clone the archive 

### ISSUE THREAD

**Issue by aryehw** [TadPath/PUMA#19]
**Describe the bug**
git clone https://github.com/TadPath/PUMA.git
fails near the end of the process - no clone is created
downloading the zip produces a 75MB file, but the archive cannot be opened by the archive manager of ubuntu

**To Reproduce**
Attempt tp clone or download zip as described above.

**Expected behavior**
a valid zip archive should be downloaded, or a clone of the main branch should be constructed.

**Desktop (please complete the following information):**
 - OS: pop os ubuntu 22.04
 - Browser: Firefox]
 - Version 101.0.1

**Additional context**
First attempt to download zip produced a 38MB file (that also was an invalid archive).

Thanks for any assistance.

**Comment by sssmc** [comment]
The zip I dowloaded via Edge was 132.8MB and the one I downloaded via wget on Ubuntu was 127MB. Looks like your download is cutting cut off for some reason. Have you tried a command like this: 
`wget https://github.com/TadPath/PUMA/archive/refs/heads/main.zip`

**Comment by aryehw** [comment]
It also failed with wget. 
It appears to be a problem with my network. I moved from wired to wireless, and managed on the second attempt to get a complete download of the zipped archive. It is 126.69 MB on my system.
Thank you for your assistance.

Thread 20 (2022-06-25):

### ISSUE TITLE
missing python module

### ISSUE THREAD

**Issue by tiarno** [TadPath/PUMA#20]
**Describe the bug**
When I load the file Focus_Gears into FreeCad 0.19, I get this traceback:
Note: This doesn't happen with the file Stage.FCStd, but does the same with Binocular.

09:43:43  Traceback (most recent call last):
  File "C:\Program Files\FreeCAD 0.19\bin\Lib\site-packages\shiboken2\files.dir\shibokensupport\__feature__.py", line 142, in _import
    return original_import(name, *args, **kwargs)
<class 'ModuleNotFoundError'>: No module named 'FastenersCmd'
09:43:43  Traceback (most recent call last):
  File "C:\Program Files\FreeCAD 0.19\bin\Lib\site-packages\shiboken2\files.dir\shibokensupport\__feature__.py", line 142, in _import
    return original_import(name, *args, **kwargs)
<class 'ModuleNotFoundError'>: No module named 'FastenersCmd'
09:43:46  Traceback (most recent call last):
  File "C:\Program Files\FreeCAD 0.19\bin\Lib\site-packages\shiboken2\files.dir\shibokensupport\__feature__.py", line 142, in _import
    return original_import(name, *args, **kwargs)
<class 'ModuleNotFoundError'>: No module named 'FastenersCmd'
09:43:46  Traceback (most recent call last):
  File "C:\Program Files\FreeCAD 0.19\bin\Lib\site-packages\shiboken2\files.dir\shibokensupport\__feature__.py", line 142, in _import
    return original_import(name, *args, **kwargs)
<class 'ModuleNotFoundError'>: No module named 'FastenersCmd'

**To Reproduce**
1. Open FreeCad 0.19
2. Open file Focus_Gears.FCStd
3. See error

**Expected behavior**
No errors on loading file

**Desktop (please complete the following information):**
 - OS:  Windows 10

**Comment by TadPath** [comment]
Hello. Thanks for this. I forgot to mention that I use the Fasteners Workbench which is an addon to FreeCAD. So perhaps if you install this addon it might fix the problem. Here are the instructions: https://wiki.freecadweb.org/Fasteners_Workbench
Please let me know if that works.

**Comment by tiarno** [comment]
What a fast response, thanks! Yes, I installed the workbench and now I no longer get the missing module issue.
I appreciate your work, I'm printing my first item now.

**Comment by TadPath** [comment]
That's great. I've now edited the FreeCAD ReadMe in the main repo for others to avoid this issue. Hope it goes well.

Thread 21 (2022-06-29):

### ISSUE TITLE
JST XH PCB headers

### ISSUE THREAD

**Issue by GanescuStefan** [TadPath/PUMA#21]
Hello,

I am currently trying to build the PCC.
In the component section of both the PCC and of the motherboard, it mentions that the JST XH PCB connector headers should be the right angled versions only, however in some images the connectors are straight. For example, on this motherboard image there are 7 straight connectors and 2 right angled ones, even though the specification says they should all be right angled. 

![MB_TP_Components](https://user-images.githubusercontent.com/71331265/176206094-11b23487-ef03-446d-aa02-f243a867d33e.png)

Is this an error with the required components, or would it be best to use the right angled versions? There are less images of the PCC connectors, so I wanted to know for sure if I needed both straight and right angled headers for each of the pin numbers.

Thank you in advance.

**Comment by TadPath** [comment]
Hello. Thanks for the question. It is not an error but could do with some explanation (I would normally provide this in the videos but I haven't released a PCC video yet so, here goes):
The key thing to note here is that the way you mount them is not the same as the pin angle. Let me explain.
You mount the headers as shown in the diagram - i.e. most of them are straight up, not 90 degrees, with two exceptions as shown). However, because with the DIY motherboard you have wires running under some of the headers on the top surface of the tripad board, this means that some of the headers that are mounted straight up will need extra long pins to make it through to the underside of the board for soldering (compared to the usual straight pin headers which have very short pins).
So if you use right-angled headers, you can always straighten the pins in the header (with long nosed pliers) to get 'straight headers' with extra long pins. You an then trim the pins on the underside of the board after soldering. 
Also, for making extension cables you need the extra length provided by the (straightened out) 90 degree headers. So I advise people just buy all 90 degree headers and be done with it. If you are using the professional PCB then you can (and should) just use the straight-pin headers for those headers that are shown fitted straight up.
Does that answer your question?

**Comment by GanescuStefan** [comment]
Yes it does, thank you very much!  Then, should all of the PCC headers also be straightened, or should some stay at a right angle too?

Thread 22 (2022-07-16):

### ISSUE TITLE
Power lamp motherboard connection

### ISSUE THREAD

**Issue by GanescuStefan** [TadPath/PUMA#22]
Hello,

I am currently trying to build the PCC and I am wondering what the "JST3 Pwr Lamp" on the motherboard is attached to. In the assembly procedure it mentions that the output of the buck converter should be connected to the lamp meter section of the motherboard, while the batteries should be connected to the motherboard "JST1 Power In" through a switch.

![image](https://user-images.githubusercontent.com/71331265/178999003-c0d2d7ef-c194-430f-a2af-1a39c4e25595.png)

Is the lamp power meant to be attached to the input of the buck converter or to some other part? I would appreciate a circuit diagram of some sort if possible, as it would be much easier to see it than through text.

Thank you in advance

**Comment by TadPath** [comment]
Hello. JST3 receives the output from the XL4015 power regulator (that is what provides power for the lamp - Pwr Lamp). As with all PUMA modules - as I state in the GitHub intro - the video will make all things clear but I have not yet finished the PCC video so it is not yet released. You may get some additional insight into lamp connections with respect to the potentiometer by looking at the pages on the PUMA Lite. Here is a photo from a screenshot of one of my video clips (from the as yet unreleased video!) showing me about to make the connection: ![image](https://github.com/TadPath/PUMA/blob/main/Electronics/Control_Console/Images/JST3.png?raw=true)

**Comment by GanescuStefan** [comment]
Thank you very much! Does this mean that the JST 9 Lamp Meter connection is attached to the input from the XL4015 power regulator instead?

**Comment by TadPath** [comment]
Sorry. I made a mistake in my last reply description - JST3 provides power to the INPUT side of the XL4015 (I edited my answer to reflect that). The photo is correct. I see that it is precarious to try and answer such questions one-by-one and probably others can't wait for the video too (it will take me a few months at least anyway to finish it) so, I made a connections diagram and posted that on the Motherboard page here on GitHub now. Please see the diagram - it should answer all your questions about connections. As for practicalities about wire lengths, insulation, techniques for making the various connections - you will have to work that out for yourself till the video comes out (you may even work out better methods than mine anyway). The video will take time because I am actually making some upgrades / alterations to the PCC (as will all PUMA modules prior to video release) so watch out for the video when it comes because you may want to update your PCC accordingly.

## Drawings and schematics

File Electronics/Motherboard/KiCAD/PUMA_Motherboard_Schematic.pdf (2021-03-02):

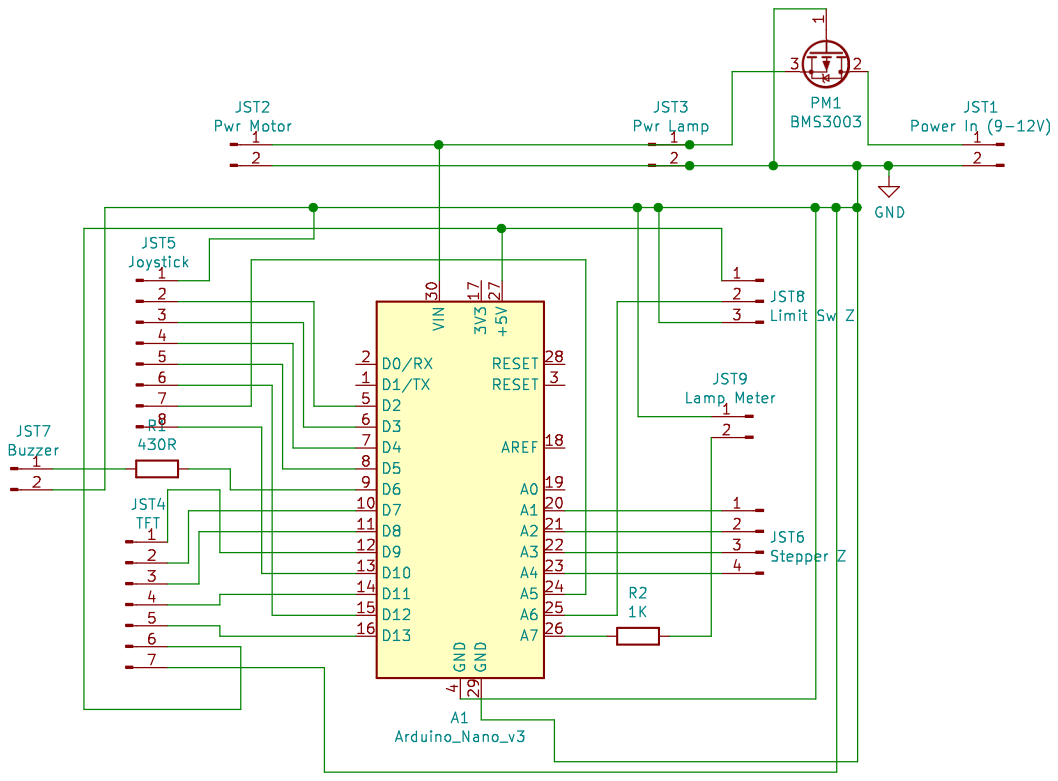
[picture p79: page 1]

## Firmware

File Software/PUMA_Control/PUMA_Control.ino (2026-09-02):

/* ****************************************************************** */
/*                                                                    */
/* PUMA Control v1.2                                                  */
/* =================                                                  */
/*                                                                    */
/* V 1.2 Is an upgraded version that has two functional changes       */
/* to v.1.1:                                                          */
/*           1. Added the ability to shift the aperture function in   */
/*              X and Y so it can be finely centred to the objective  */
/*              back focal plane.                                     */
/*           2. The ammeter function is now disabled at boot up by    */
/*              default (but you can still switch it on at any time   */
/*              via the 'Defaults' menu.                              */
/* I have had to make some general alterations to some functions to   */
/* make them more byte-efficient (generate a smaller size binary) in  */
/* order to fit in the new aperture shifting code but those changes   */
/* should not affect functionality.                                   */ 
/* Other features are identical to v 1.1.                             */
/*                                                 PJT 15.07.2026     */
/*                                                                    */
/* ------------------------------------------------------------------ */
/*                                                                    */
/* PUMA Control v1.1                                                  */
/* =================                                                  */
/*                                                                    */
/* V 1.1 is the first full release (after the pre-release).           */
/* Compared to v1.0 is has all the same feature plus the ability to   */
/* set different colours for the various components of the aperture   */
/* function of the SLM thereby allowing the easy use of custom        */
/* Rheinberg filters.                                                 */
/* You also now have the option of setting a custom colour which can  */
/* be assigned to anything that takes a colour. The custom colour     */
/* value is defined via the Defaults menu. Multiple custom colours    */
/* can be used simultaneously (see Manual for how to do this).        */
/* In light of the fact that the ammeter readings can be spuriously   */
/* high and unreliable when batteries are useed, this version gives   */
/* you the option to diable the ammeter although this option must be  */
/* used with caution because you will loose the warning of a power    */
/* regulator failure that could blow the LED light source. See the    */
/* user's Manual for details.                                         */
/* Other features are identical to v 1.0.                             */
/*                                                 PJT 31.07.2021     */
/*                                                                    */
/* ------------------------------------------------------------------ */
/* Description for v 1.0                                              */
/*                                                                    */
/* This is the source code for the Arduino Nano to run the control    */
/* operations for the Optarc PUMA microscope.                         */
/*                                                                    */
/* This software performs the following functions:                    */
/* > Allows the user to control the Z-stage focus motor via the 5-way */
/*   joystick controller.                                             */
/* > Drives the ST7789 TFT display screen for the AR module.          */
/* > Provides the GUI for menu navigation to select various functions */
/*   and user modes.                                                  */
/* > Provides an interactive pointer so the user can demonstrate      */
/*   structures of interest to other viewers.                         */
/* > Provides the ability to mark and count objects interactively.    */
/* > Provides the ability to measure objects - either counts, angles  */
/*   or arbitrary line and boundary length measurements in calibrated */
/*   units.                                                           */
/* > Provides the ability to display a number of custom grids, scale  */
/*   bars and graticules in a user-selectable scale and colour.       */
/* > Provides the ability to display a plain backgound in a number of */
/*   colour options to act as illumination for low power projection   */
/*   of specimens via the AR projector (with the appropriate slide    */
/*   holder adapter in place).                                        */
/* > Provides a timer facility.                                       */
/* > Provides some aperture control functions for use with a PUMA SLM */
/*   filter (spatial light modulator aperture control).               */
/* > Provides the ability to integrate several of the above functions */
/*   so they can be used simultaneously.                              */                               
/*                                                                    */
/* For full functionality the user must have the PUMA Augmented       */
/* Reality module (AR Module) installed on their scope because this   */
/* contains the TFT display which shows all graphical feedback and so */
/* allows the user to see the GUI menus and select their functions.   */
/* However, the default mode of operation when powered up is Z-motor  */
/* control so even if you do not have the AR Module you can still use */
/* the joystick to control the focus motor without any visual         */
/* feedback but most of this software's functionality will not be     */
/* available to you. It is possible to connect a bare ST7789 TFT      */
/* screen to the control box to get visual feedback provided the TFT  */
/* screen can run on 5v (3v only models must not be used because the  */
/* control box supplies 5v to the TFT screen and 3v only models will  */
/* be permanently destroyed if connected). However, if this is done,  */
/* be aware that all textual information will be in mirror writing    */
/* because the display is designed for viewing via the AR projector   */
/* and the AR projector gives a mirror image of the screen to the     */
/* viewer. Thus you will need to view the screen via a mirror to see  */
/* easily readable information.                                       */
/*                                                                    */
/* This program uses a modified version of the Adafruit GFX library   */
/* where the default font has been customised to draw mirror writing  */
/* and also to draw custom graphics characters. I place this custom   */
/* version into a copy of that library called GFXM (in the libary     */
/* folder GFXM_Library) so that this does not get overwritten each    */
/* time the standard Adafruit graphics library is updated). This also */
/* includes its own version of the standard Arduino library Print.cpp */
/* file which ensures writing is right to left - i.e. mirrored.       */
/* This also uses a slightly modified version of  Pawel A. Hernik's   */
/* "Arduino_ST7789_Fast" library which I made called 'ST7789_FastM'   */
/*                                                                    */
/*           This program was written by Dr P. J. Tadrous  20.11.2020 */
/*                                               Last edit 08.07.2021 */
/*                                                                    */
/* ****************************************************************** */

// 'Puma_115_x_144', 115x144px, 23 chars across x 18 chars down
const unsigned char PumaIcon [] PROGMEM = {
32, 11, 176, 177, 178, 179, 32, 8, 180, 181, 182, 183, 181, 181, 181, 184, 182, 185, 186,
225, 2, 187, 188, 32, 8, 189, 225, 12, 190, 32, 9, 225, 13, 191, 192, 32, 8, 225, 14, 193,
194, 195, 32, 6, 225, 16, 196, 197, 195, 32, 4, 225, 18, 191, 32, 4, 225, 19, 198, 32, 3,
225, 19, 199, 32, 3, 225, 19, 200, 201, 32, 2, 225, 20, 202, 32, 2, 225, 21, 203, 195,
225, 22, 204, 225, 22, 187, 225, 21, 205, 206, 207, 208, 208, 208, 208, 209, 210, 211, 212,
213, 225, 9, 214, 215, 216, 32, 10, 217, 218, 225, 6, 219, 220, 32, 15, 221, 222, 223, 225,
1, 214, 224, 0 };

#include <limits.h>

// For TFT Screen functionality
#include <SPI.h>
//#include <SD.h>
#include <GFXM.h> // Adafruit's GFX library modified to write mirror-flipped text and numbers.
#include <ST7789_FastM.h> // Pawel A. Hernik's fast ST7789 library modified for mirror-flipped text and numbers.

#define TFT_DC    7
#define TFT_RST   8
#define TFT_BLK   9
#define SCR_WD   240
#define SCR_HT   240
#define CS_ALWAYS_LOW

#define SCR_WD 240
#define SCR_HT 240
Arduino_ST7789 lcd = Arduino_ST7789(TFT_DC, TFT_RST);

// For Joystick controller functionality
#define NAVI_UP    2
#define NAVI_DOWN  3
#define NAVI_LEFT  4
#define NAVI_RIGHT 5
#define NAVI_MID   12
#define NAVI_SET   A5
#define NAVI_RST   10
// The following are arbitrary values used as ID flags
// for simultaneous press events
#define NAVI_UPLEFT    32
#define NAVI_UPRIGHT   33
#define NAVI_DOWNLEFT  34
#define NAVI_DOWNRIGHT 35
#define NAVI_SETRST    36
#define NAVI_SETDOWN   37
#define NAVI_SETUP     38
#define NAVI_SETLEFT   39
#define NAVI_SETRIGHT  40
#define NAVI_SETMID    41

// For the sound buzzer
#define BUZZER 6

// For the light meter
#define LAMP_METER  A7

// For Z-Motor functionality
#define ZMOTOR_PIN_1 A1
#define ZMOTOR_PIN_2 A3
#define ZMOTOR_PIN_3 A2
#define ZMOTOR_PIN_4 A4

// Control Modes
// These #defines must be in the same order as the #defines for
// the menu levels 'ML_...' (which see)
#define CM_Z_MOTOR      1
#define CM_POINTER      2
#define CM_TIMER        3
#define CM_GRATICULE    4
#define CM_PLAIN        5
#define CM_APERTURE     6
#define CM_MENU_DELTA   6
// NB: The 'CM_MENU' (not #defined) is anything > CM_MENU_DELTA from
//     (CM_Z_MOTOR + CM_MENU_DELTA) to (CM_GRATICULE + CM_MENU_DELTA).
//     Simply subtract CM_MENU_DELTA from the current Control_mode value
//     to get the Control_mode the program was in prior to entering the
//     'CM_MENU'.
//     The 'CM_MENU' is entered into by simply adding CM_MENU_DELTA to 
//     the current (non-menu) Control_mode.
//     This way the program 'knows' what mode it was in prior to 
//     entering the menu mode and so can return to that mode if menu is 
//     exited without changing the control mode (e.g. due to a timeout 
//     or if the menu items changed did not include the control mode) -
//     without the need for a second global variable keeping track of 
//     what the previous control mode was. Clearly, if the user selects
//     a new control mode while in the menu mode, this will be recorded
//     in the Control_mode global as the selected CM + CM_MENU_DELTA
//     until the user exits the Menu CM (at which point CM_MENU_DELTA 
//     will be subtracted from Control_mode to activate the currently
//     selected control mode). I also do it this way so if, in future, I
//     add further control modes beyond the current maximum value
//     (CM_GRATICULE in this case) I can simply change CM_MENU_DELTA to
//     equal the new maxmimum value and recompile.

// Pointer Characters
#define PC_ARROW_1 0x18 
#define PC_ARROW_2 0x19 
#define PC_ARROW_3 0x1a 
#define PC_ARROW_4 0x1b 
#define PC_ARRHD_1 0x10 
#define PC_ARRHD_2 0x11 
#define PC_ARRHD_3 0x1e 
#define PC_ARRHD_4 0x1f 
#define PC_ARRHD_5 0xae 
#define PC_ARRHD_6 0xaf 
#define PC_CURSR_1 0x2b 
#define PC_CURSR_2 0x58 

// Marker Characters
#define MC_ASTER_1  0x2a 
#define MC_ASTER_2  0x2b 
#define MC_CIRCLE 0x4f 
#define MC_HASH   0x23 
#define MC_CROSS  0x58 
#define MC_PIXEL    0x00
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

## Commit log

2021-10-13 Use DI_IFD_Tray instead of twice DI_IAD_Tray in MD_DI_Kohler
    [PUMA_Bill_of_Materials.xls]
2021-10-15 Included missing DI_LC_Collar models
    Included missing DI_LC_Collar_2.stl and DI_LC_Collar_7.stl models in:
    + List of STL Files
    + MD_DI_Kohler
    + MD_DI_Epiillumination
    + MD_DI_Polarisation
    [PUMA_Bill_of_Materials.xls]
2021-10-23 Corrections to quantities for pol
    Fixed an error that used the wrong number of parts for the polarising illuminator(s)
    Added a sheet for the trans-polarisation illuminator (only epi-polarisation was represented before)
    Separated out the components for the LED illuminator and 2x23 mm collector in the sheets for ease of reading
    [PUMA_Bill_of_Materials.xls]
2021-11-25 Updates to Kohler Illuminator etc.
    Updates to Kohler Illuminator models and module included.
    Specific example source for thin lens of Low Power Collector provided (this is slightly different to the original v.1 specs).
    [PUMA_Bill_of_Materials.xls]
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2021-11-29 Spellcheck run on Köhler Illuminator specs doc
    Some typos fixed and the document date font replaced because it did not print in the PDF
2021-12-22 Corrections to Long Legs System parts
    Fixed an error in the grub screw size for the Hind Extension component (M4 grub screw is required, not M3 as previously stated).
    Removed the requirement for 6 M6 washers from the Long Legs system (they are not required - they may be used but the assembly is less prone to loosen itself without them so it is preferred to avoid t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
    [PUMA_Bill_of_Materials.xls]
2021-12-27 Fixed Long Legs M3 screw requirements
    Fixed an error which gave wrong requirements for the M3 screws for the Long Legs stand systems.
    [PUMA_Bill_of_Materials.xls]
2022-01-07 Added size info for oval mirror
    [PUMA_Bill_of_Materials.xls]
2022-01-20 Updated models and support instruction correction
    The support instruction for the simple filter block was wrong - this has now been fixed.
    Updated models: BN_Outlet_upper, BN_Splitter_block
    New model: Ocular_base_thread_R
    Name changes: BN_Ocular_base_thread changed to BN_Ocular_base_thread_L. The legacy version number was dropped from the 'Binocular' file.
2022-01-20 Some error corrections and model updates.
    Incorporates updated beam splitter models for the binocular head.
    [PUMA_Bill_of_Materials.xls]
2022-02-14 Added new models and corections
    C-mount ocular models added (to Monocular)
    Side port separate EpiStop added (to Filterblock)
    Some typos fixed and minor edits to text.
2022-02-14 C-mount monocular module and EpiStop added
    C-mount monocular models added
    Side port separate EpiStop model info added (for the advanced filter block for epi-illumination)
    [PUMA_Bill_of_Materials.xls]
2022-02-14 Delete Monocular_v1.1.FCStd
    New version without the legacy version number added instead
    [Monocular_v1.1.FCStd]
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2022-02-14 Updated Filterblock and Monocular files
    Replaced with newer version
2022-03-03 DI_Condensor_23_30 modification for 30 mm lens
    Added freecad file and images to show the result of this modification. The 30 mm plano convex lens from Ali Express I received had a broader, tapered edge. The modified model allows for a good fit as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
    (https://de.aliexpress.com/item/32949791660.html?gatewayAdapt=glo2deu&spm=a2g0o.order_detail.0.0.30cb63683Ny4Z0)
    [DI_Condensor_23_30_modified.FCStd]
2022-03-05 Delete DI_Condensor_23_30_modified.FCStd
    deleting file because it is not parametric as required by the PUMA standard
    [DI_Condensor_23_30_modified.FCStd]
2022-03-05 DI_Condensor_23_30 revision
    Parametric FreeCAD model with the proposed model change (kindly provided by PJT on my behalf)
    [DI_Condensor_23_30_modified.FCStd]
2022-03-23 Monocular and Binocular models updated
    New models incorporated and ergo-monocular module added. Other ocular head modules updated to coincide with the release of the 'Ocular Heads' video.
    [PUMA_Bill_of_Materials.xls]
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2022-04-06 Updates to trinocular, monocular and Dominus
    Updated and new trinocular port parts added.
    DI_Uber_pol polariser added.
    C-mount extension for 170 mm tube lenses added.
    [PUMA_Bill_of_Materials.xls]
2022-04-06 Updates to Trinocular, Monocular and Dominus
    Trinocular adapter revised and new C-mount version added. File legacy version number removed.
    Monocular: Added the new C-mount extension for 170 mm tube length objectives.
    Dominus: Added the new DI_Uber_pol model for polarisation with the Abbe condenser. Also, legacy file version names removed.
    [Trinocular_CP.FCStd]
2022-04-06 Removed old version
    [Trinocular_CP_v1.FCStd]
2022-04-07 Trinocular datasheet updated
    [PUMA_Bill_of_Materials.xls]
2022-04-09 AR Stabiliser screw length updated to 14 mm
    The M4 screw for the front of the focus plate (to hold the AR clip thumb wheel) should be 14 mm long not 12 as previously stated.
    [PUMA_Bill_of_Materials.xls]
2022-04-16 Updated polariser supplier
    Updated web link to supplier of polariser sheets
    [PUMA_Bill_of_Materials.xls]
2022-04-20 Updated AR Projector and Monocular sections
    Incorporating resource stats for the new and modified AR Projector and Monocular module models.
    Removed AR_Clip_lock (no longer used - it's functionality has been incorporated into the new AR_Clip model).
    [PUMA_Bill_of_Materials.xls]
2022-05-12 Updated Stage baseplate and Z-Motor Yoke
    Stage baseplate - added three holes for optimum fit of high quality all-metal XY Vernier mechanical slide holder.
    Z-Motor Yoke - modified the part that fits onto the hex head of the bolt to employ a flexible fitting that should work well and easily even with slight variations of 3D print and bolt head dimensions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
    [Z_Motor.FCStd]
2022-05-12 Updates to ST_Base_plate and ZM_Z_Yoke
    Updated Cura 3D print costs for:
    * ST_Base_plate with new holes for all-metal XY Vernier slide holder
    * Modified ZM_Z_Yoke
    [PUMA_Bill_of_Materials.xls]
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2022-05-18 Updates to Dominus Condenser
    Improved models for the 23 30 condenser and its attachments - mechanical improvements and easier acceptance of the 30 mm lens.
    30 mm lens receptacle is now spring loaded to cope with slight variations in dimensions of lenses and printer tolerances.
    There is also a means to eject the lens without destroying the print.
    Slot imporved for easier insertion of IAD filters into slot.
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2022-05-18 Updated condenser models and objective specs
    Updated condenser models and added a x4 objective sheet for the basic config (was using x40 but that is not appropriate without a condenser).
    Also added some specs for objectives.
    [PUMA_Bill_of_Materials.xls]
2022-05-18 Delete DI_Condensor_23_30_modified.FCStd
    Updated condenser files incorporated into main FreeCAD files
    [DI_Condensor_23_30_modified.FCStd]
2022-05-18 Correction to quantities for MD_Ocular
    Correction to quantities for MD_Ocular printed parts
    [PUMA_Bill_of_Materials.xls]
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2022-08-23 Updated ocular heads parts
    Correction of 1 mm undershoot error.
    [PUMA_Bill_of_Materials.xls]
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2022-08-23 Updated ocular head parts
    Correction of 1 mm undershoot error. Parts modified are:
    Monocular:
    MN_Monocular_tube_c_adhesin - 1 mm shorter.
    MN_Monocular_tube_CM_c_adhesin - 1 mm shorter
    Binocular:
    BN_CM_Tube_short_c_adhesin - 1 mm shorter
    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
    [Trinocular_CP.FCStd]
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2022-08-28 Improved anti-reflection tubes and PCC
    PC_Monit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
    [PUMA_Bill_of_Materials.xls]
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2022-09-19 Error corrected in trinocular config
    The Trinocular worksheet was still pointing to the ocular cap spacer used in the binocular and ergo-monocular configs.
    That has now been fixed and it points to the thicker spacer that is required for correct set up of the trinocular config.
    [PUMA_Bill_of_Materials.xls]
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2023-02-15 Daylight Köhler adaptor added
    [PUMA_Bill_of_Materials.xls]
2023-02-28 Added Stabiliser, updated AR_Stay_thumbwheel
    [Stabiliser.FCStd]
2023-02-28 Added Stabiliser module, updated AR_Stay_thumbwheel
    [PUMA_Bill_of_Materials.xls]
2023-06-02 M4 nuts added to Z-motor sheet
    The two M4 nuts needed to secure the motor to its platform were previously omitted by mistake.
    This has been remedied.
    [PUMA_Bill_of_Materials.xls]
2023-06-16 Köhler parts update
    Köhler parts update
    [PUMA_Bill_of_Materials.xls]
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2023-07-20 Added models for PWG and high NA illuminator
    [PUMA_Bill_of_Materials.xls]
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2025-06-29 Added CNC Stage parts
    [PUMA_Bill_of_Materials.ods]
2025-06-29 Delete Bill_of_Materials/PUMA_Bill_of_Materials.xls
    Switchover to ODS format.
    [PUMA_Bill_of_Materials.xls]
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2025-06-29 CNC Stage Base dims document added
    [CNC_Stage_Base_holes.FCStd]
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2025-06-30 Updated CNC stage and non-printed parts sections
    [PUMA_Bill_of_Materials.ods]
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
